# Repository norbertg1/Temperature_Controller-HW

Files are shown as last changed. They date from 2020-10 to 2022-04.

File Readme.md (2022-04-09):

# Temperature controller - HW

This is a temperature stabilizer (PID controller) for thermoelectric cooler (Peltier module) or ceramic heater modul based on STM32F3 microprocessor and buck converter. The repository consist from a project of **schematic** and **PCB design** files made in Altium Designer. All parts includes LCSC part number ready for manufacturing with JLCPCB.

See also:\
[Temperature controller firmware](https://github.com/norbertg1/Temperature_Controller-FW)\
[Temperature controller software](https://github.com/norbertg1/Temperature_Controller-SW)

**Features:**
 - 1.5 A and 5 A output current
 - Various NTC, PTC temp. sensor support
 - 16 bit ADC for temp. sensor
 - I2C temp. sensor support (BMP280, etc..)
 - Current, voltage and power sense for both outputs
 - PID loop
 - STM32F373
 - Vref with LM4041 1.225 V for better temp. sensing
 - OLED screen SSD1306
 - Control over serial port with PC

### Block schematic:

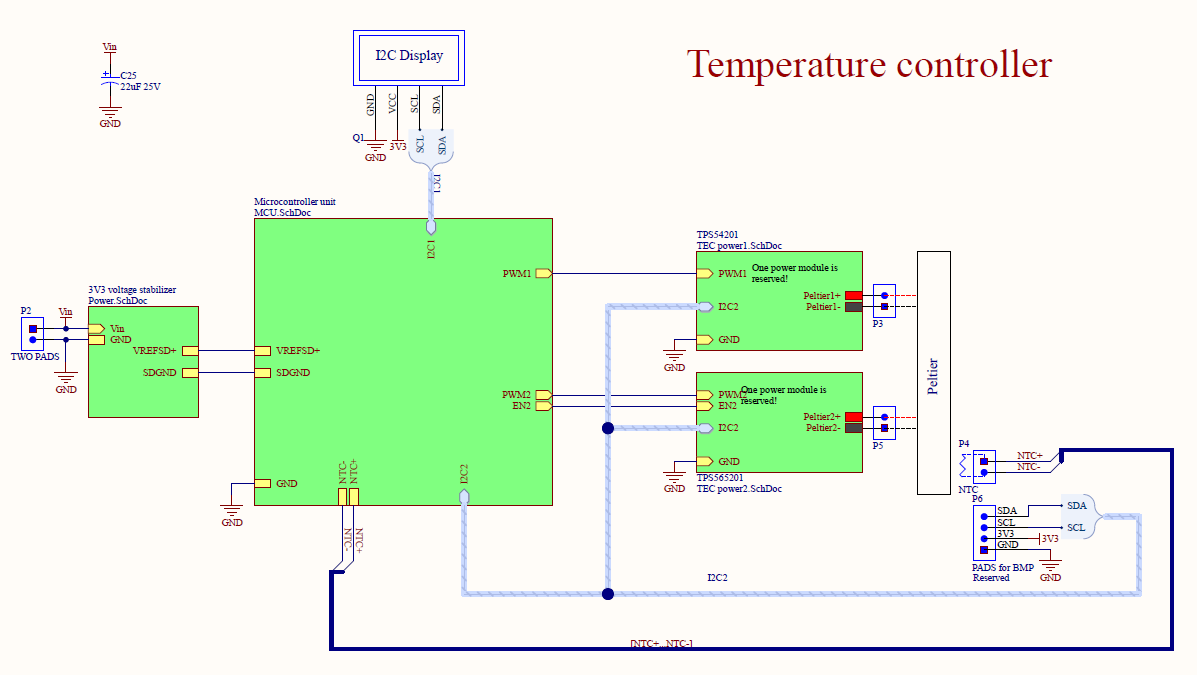
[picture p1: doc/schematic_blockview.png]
 \
Detailed hardware schematic [here](/doc/Temperature_controller.pdf).
### Use case

Original purpose for this project was cooling or heating and very precise stabilizing radiation detector and preamp input FET temperature, but its can be reused for anything else where the cooling or heating power is enough.

### Output power

The circuit is designed with two outputs:
 - **TPS54200**
Maximum output current is 1.5 A. Use this for less cooling power required applications, with more precious temp. control.
 - **TPS56201**
Maximum output current is 5 A. For utilizing the whole amount of this current need to replace the inductor with bigger one, with this one the maximum current is about somewhere 2-3 A.See datasheets and parameters.xlsx for exact components.

All the two ouputs are equiped with current sense shunt and current sense amplifier (INA226) communicating through I2C.

### Temperature sensing

Two options:
 - **BMP280:** Fully digital readout over I2C. Disadvantage is that you need 4 wires, and maximum and minimum values are determined by datasheet (-40 °C and 85 °C).

 - **PTC, NTC:** Precise 1.225 V is produced by IC for Vref and for power Rx and NTC modules. Differential ADC used for mesure the voltage of Rx and NTC modules. From the included temperature vs. resistance (R-T) table the temperature can be determined.
Also any part can be used that withstand the temperature and the R-T curve is known or measured.

### Programming

Programming through SWD connector with STlink v2:\

SWDIO — SWDIO\
SWCLK — SWCLK\
GND — GND

### Control loop
In very short:\
Read the temperature --> calculate the error from desired temp --> adjust the output power\
For software see the [related repository](https://github.com/xnorbi/Temperature_Controller-SW).

### Assembled PCB



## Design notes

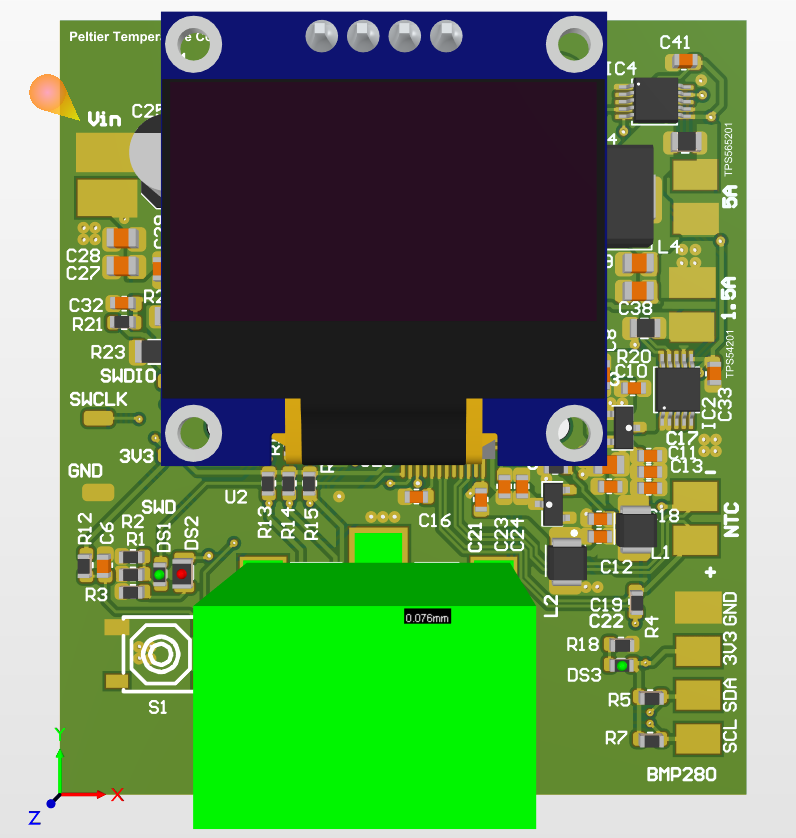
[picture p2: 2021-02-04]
doc/PCB_altium3D.png

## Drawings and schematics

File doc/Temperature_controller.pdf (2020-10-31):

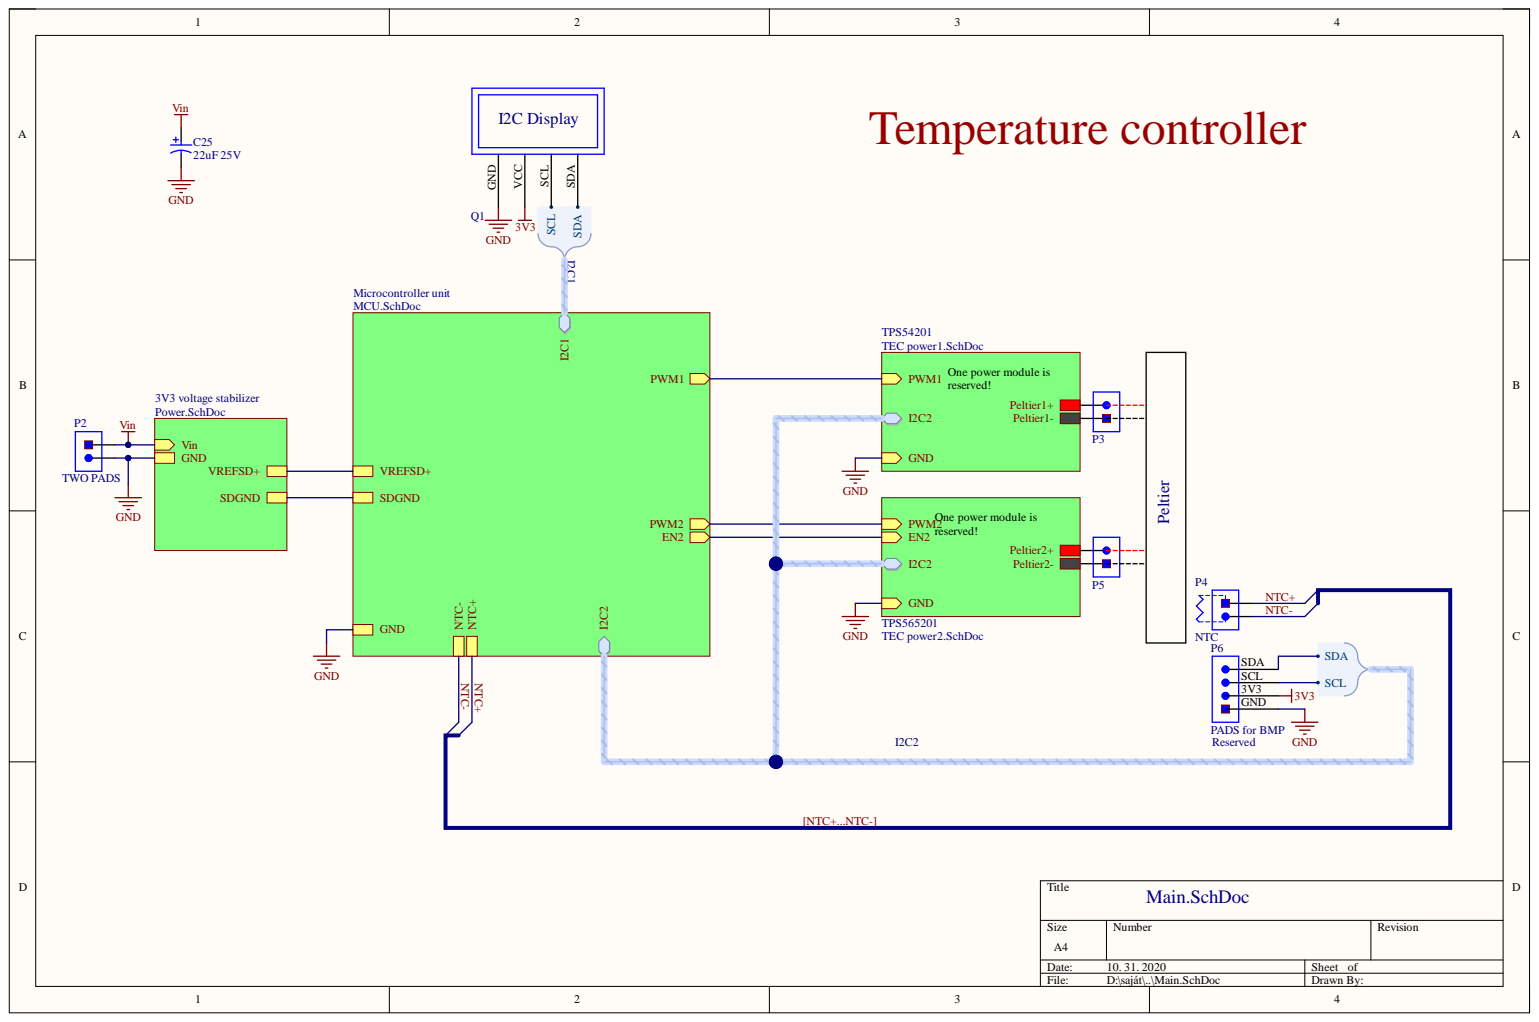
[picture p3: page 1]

One power module is
reserved!

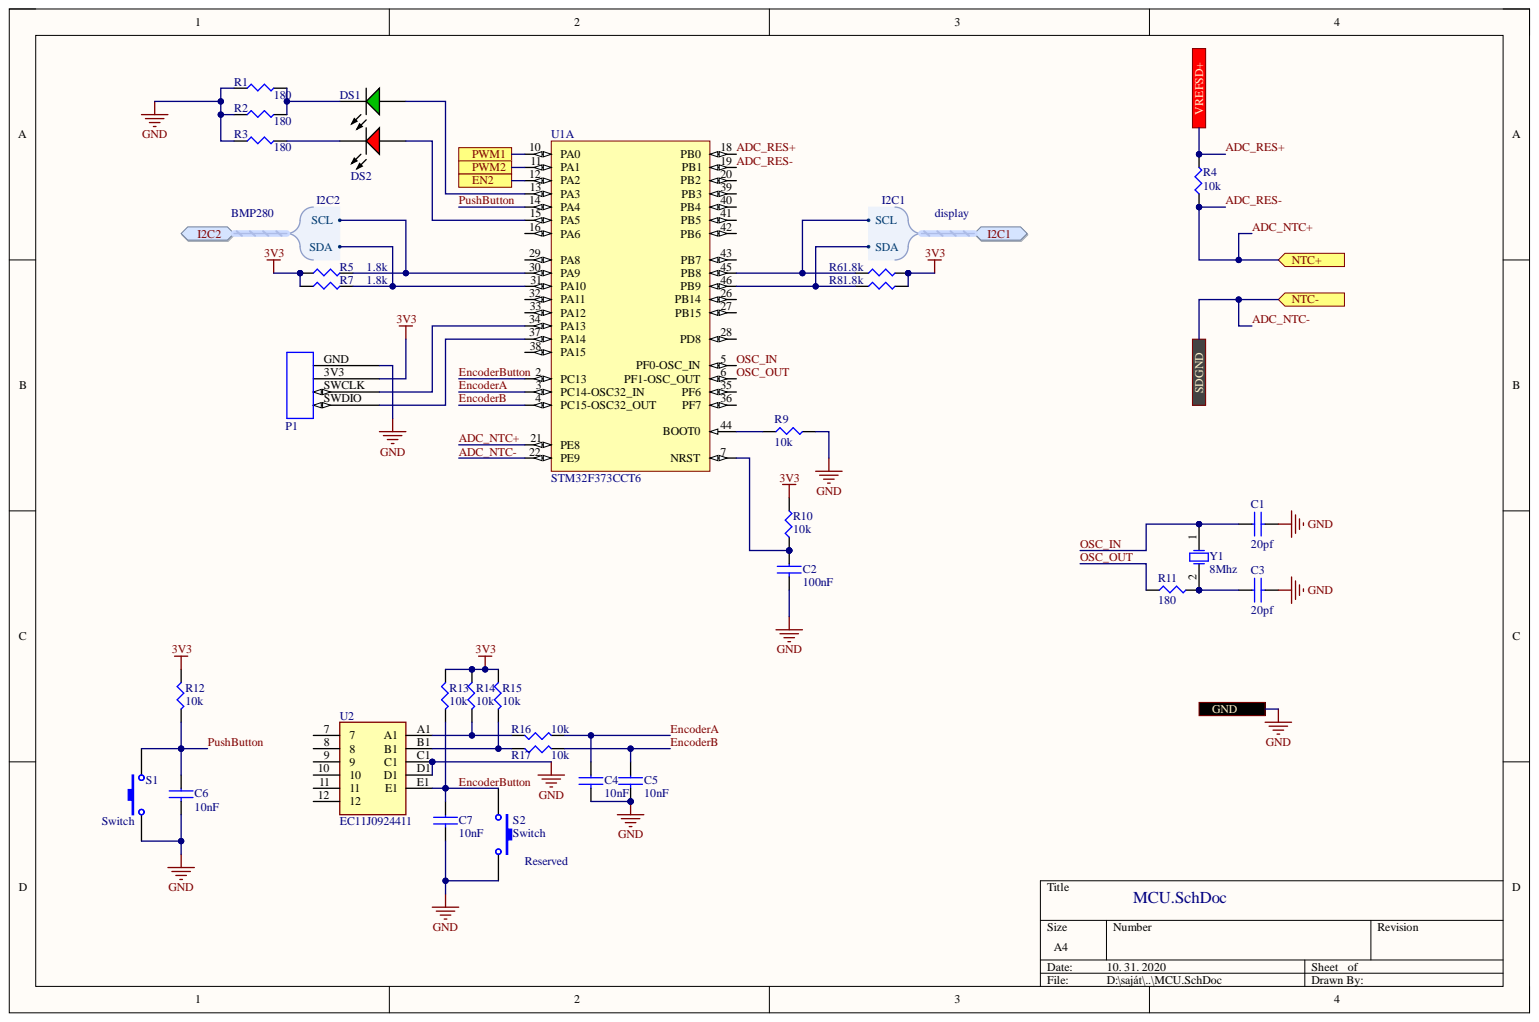
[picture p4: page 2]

EncoderButton

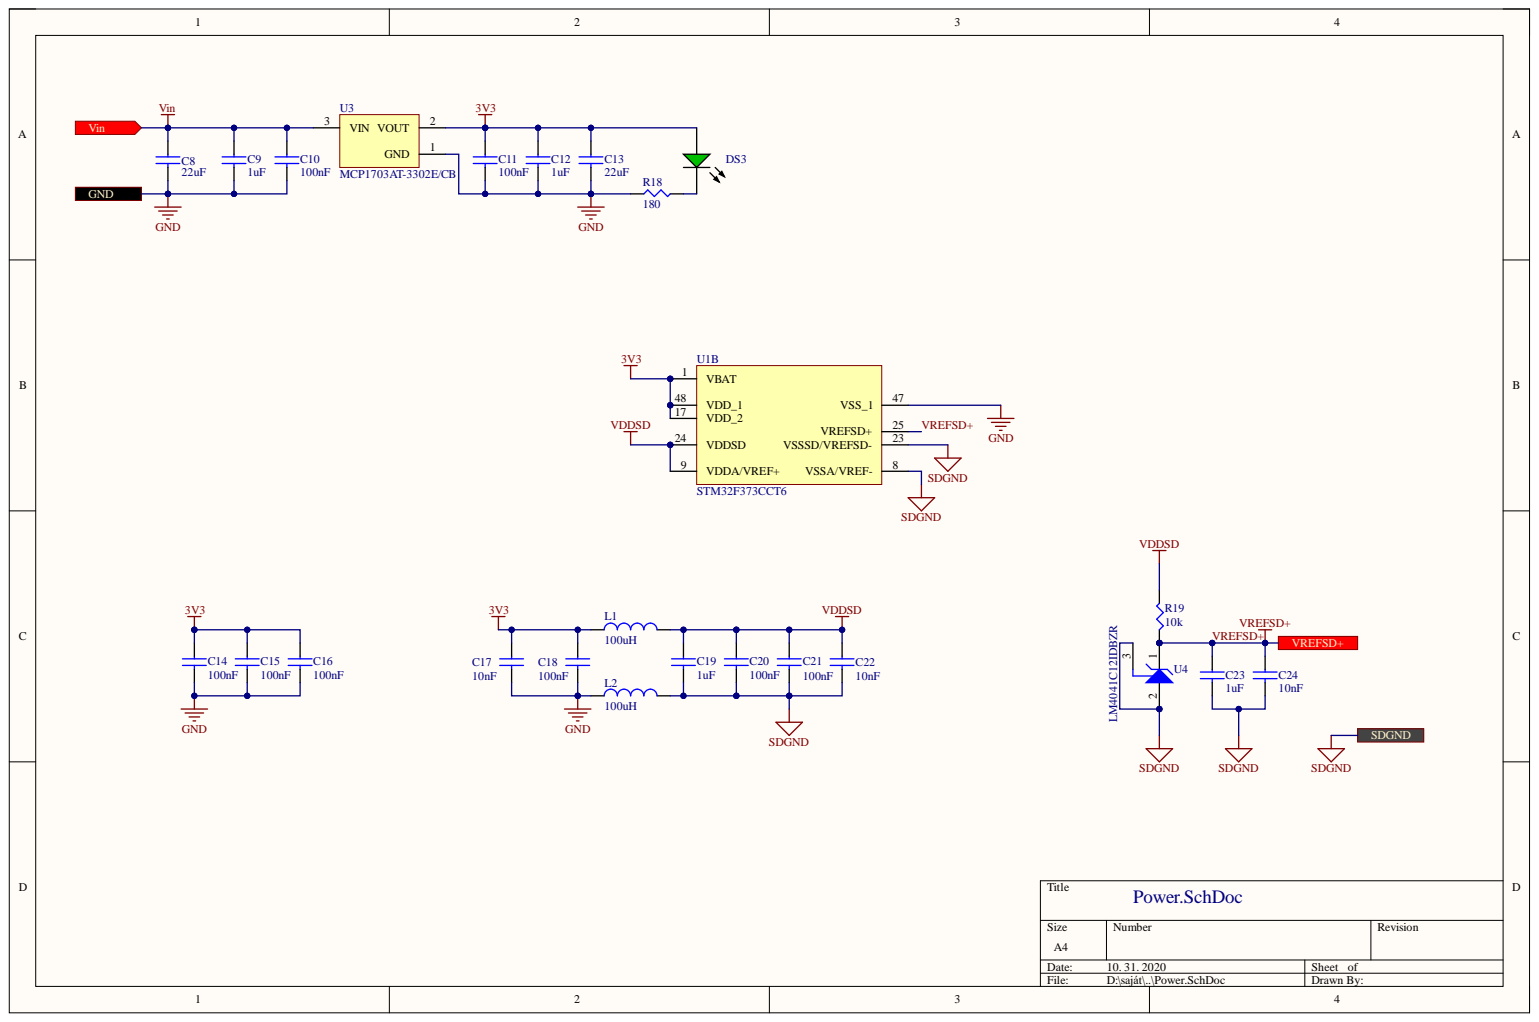
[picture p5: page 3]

VDD_2 17 VDD_1 48

VDDSD 24

VDDA/VREF+ 9

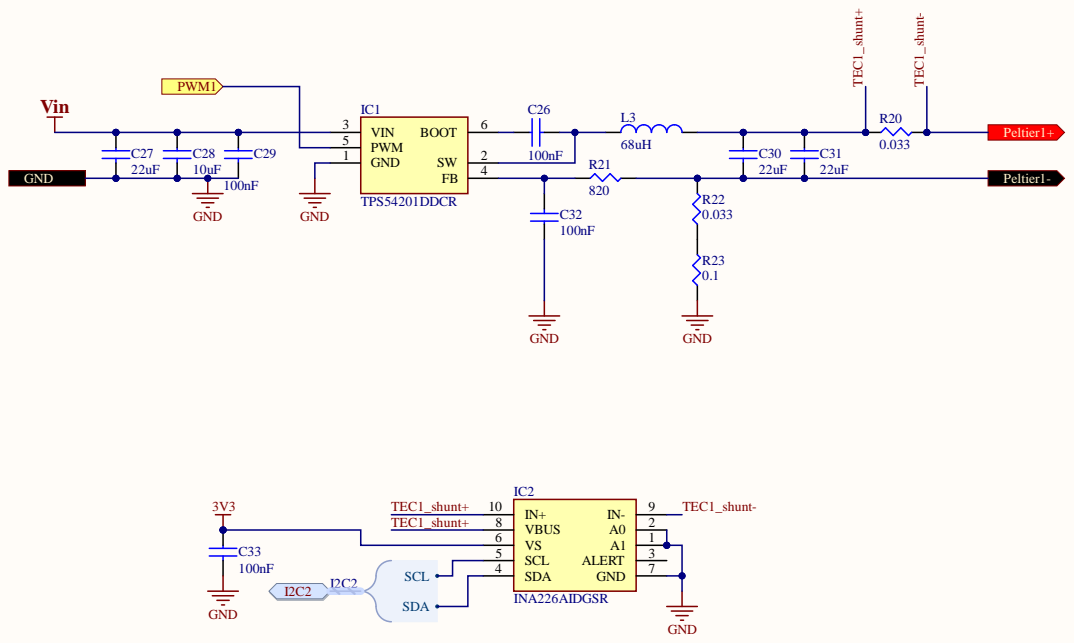
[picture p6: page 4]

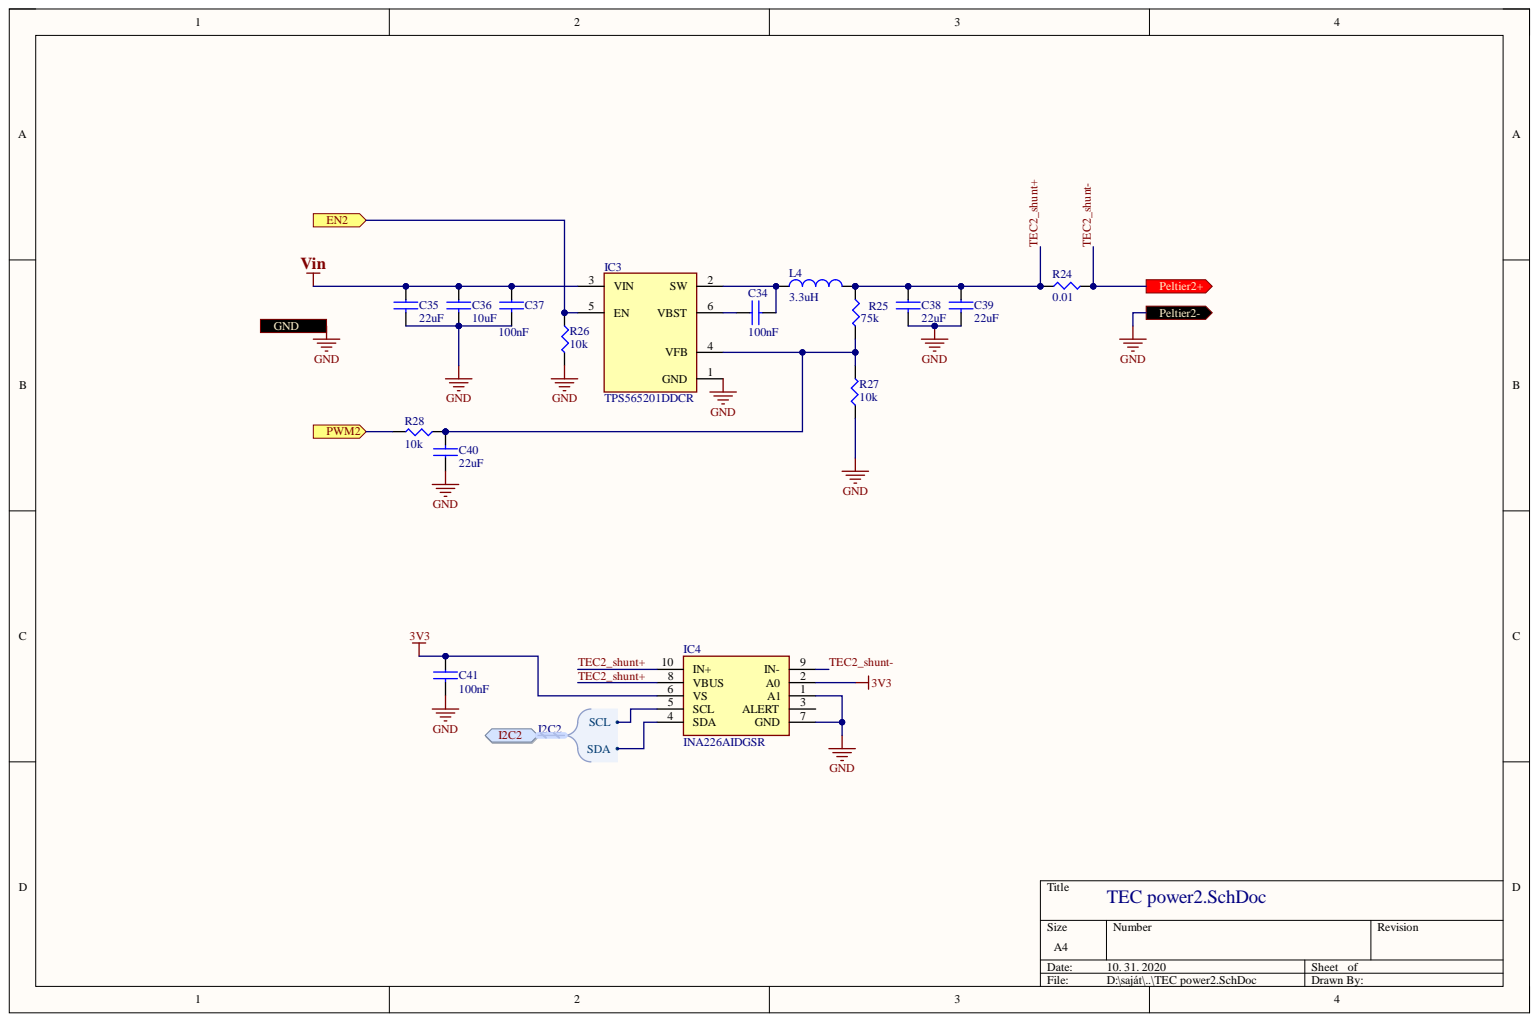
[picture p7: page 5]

C35 C36 C37
22uF | 10uF 100nF | R26 10k

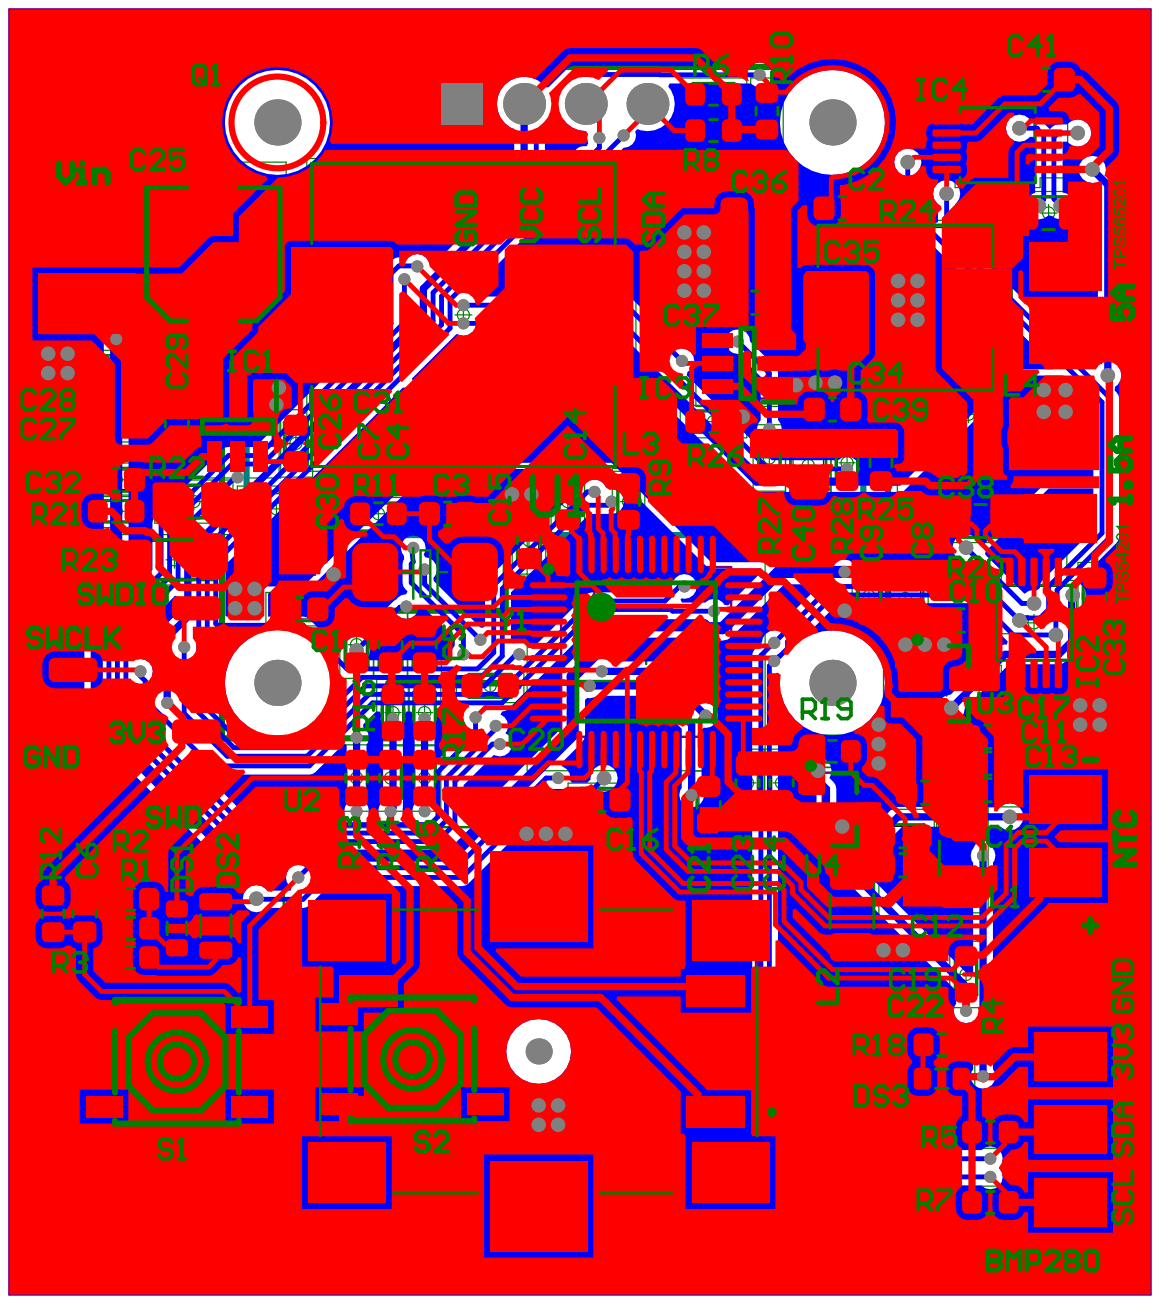
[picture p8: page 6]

Comment | Quantity | Designator | LCSC Part # | Footprint | Description | LibRef
100nF | 16 | C2, C10, C11, C14, C15, C16, C18, C20, C21, C26, C29, C32, C33, C34, C37, C41 | C14663 | CAPC160X80X90L35N | | capacitor
10k | 13 | R4, R9, R10, R12, R13, R14, R15, R16, R17, R19, R26, R27, R28 | C25804 | RESC160X80X90L30N | | Resistor
22uF | 9 | C8, C13, C27, C30, C31, C35, C38, C39, C40 | C45783 | CAPC200X125X110L50N | | capacitor
10nF | 7 C4, C5, C6, C7, C17, | C22, C24 | C57112 | CAPC160X80X90L35N | | capacitor
180 | 5 R1, R2, R3, R11, R18 | | C22828 | RESC160X80X90L30N | | Resistor
1uF | 4 C9, C12, C19, C23 | | C15849 | CAPC160X80X90L35N | | capacitor
1.8k | 4 R5, R6, R7, R8 | | C4177 | RESC160X80X90L30N | | Resistor
0.033 | 2 R20, R22 | | C127689 | RESC200X125X70L40N | | Resistor
10uF | 2 C28, C36 | | C15850 | CAPC200X125X110L50N | | capacitor
19-217/GHC-YR1S2/3T | 2 DS1, DS3 | | C72043 | LEDC160X80X60L30N | Green LED | LED
20pf | 2 C1, C3 | | C1648 | CAPC160X80X90L35N | | capacitor
100uH | 2 L1, L2 | | C333986 | INDC320X160X210L60N | Inductor | Inductor
INA226AIDGSR | 2 IC2, IC4 | | C49851 | SOP10P50_300X490X110L55X22N | Integrated Circuit | INA226AIDGSR
Switch | 2 S1, S2 | | | Tactile switch | Switch | Switch
TWO PADS for TEC | 2 P3, P5 | | | TWO PADS | | TWO PADS for TEC
#NAME? | 1 C25 | | C249771 | PNSC-FP-V-C_V | Aluminum Electrolytic Capacitor, 22 uF, +/-20%, 25 V, 2-Pin SMD (Size Code C), -55 to 105 degC, RoHS, Tape and Reel | CMP-2000-06213-1

0.01 | 1 R24 | | C127689 | RESC200X125X70L40N | | Resistor
0.1 | 1 R23 | | C25334 | RESC310X152X65L45N | | Resistor
3.3uH | 1 L4 | | C280586 | INDM730X660X300L160X290N | Inductor | Inductor
8Mhz | 1 Y1 | | C115962 | 5032 | Crystal Oscillator | XTAL
68uH | 1 L3 | | C169377 | INDM1250X1250X800L290X540N | Inductor | Inductor
75k | 1 R25 | | C46216 | RESC160X80X90L30N | | Resistor
820 | 1 R21 | | C23253 | RESC160X80X90L30N | | Resistor
EC11J0924411 | 1 U2 | | | EC11J0924411 | Rotary encoder | EC11J0924411
FC-2012HRK-620D | 1 DS2 | | C84256 | LEDC200X125X110L30N | Red LED | RED LED
LM4041C12IDBZR | 1 U4 | | C133587 | DBZ0003A_N | Precision Micropower Shunt Voltage Reference, 0.5% accuracy, 1.2 V, 15 ppm / degC, 12 mA, -40 to 85 degC, 3-pin SOT-23 (DBZ), Green (RoHS & no Sb/Br) | CMP-0366-00994-2
MCP1703AT-3302E/CB | 1 U3 | | C144183 | SOT-23A-CB3_M | | CMP-0136-00758-1
NTC | 1 P4 | | | TWO PADS | | TWO PADS for NTC
PADS for BMP | 1 P6 | | | FOUR PADS | | PADS for BMP
SSD1306OLED_big | 1 Q1 | | | SSD1306OLED | I2C display | SSD1306OLED_big
STM32F373CCT6 | 1 U1 | | C89403 | STM-LQFP48_L | ARM Cortex-M4 32-bit MCU, 256 KB Flash, 32 KB Internal RAM, 36 I/Os, 48-pin LQFP, -40 to 85 degC, Tray | STM32F373CCT6
SWD | 1 P1 | | | SWD | | SWD port
TPS54201DDCR | 1 IC1 | | | SOT95P280X110-6N | Integrated Circuit | TPS54201DDCR_1
TPS565201DDCR | 1 IC3 | | | SOT95P280X110-6N | Integrated Circuit | TPS565201DDCR
TWO PADS | 1 P2 | | | TWO PADS - medium | | TWO PADS

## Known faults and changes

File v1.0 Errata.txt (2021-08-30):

SWDIO and SWCLK swapped	✔2020.11.20
crystal change to 32 Mhz ---> not necessary google for benefits
LM4041 wrong footprint
R25 wrong part number its below 1ohm

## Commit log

2020-10-13 Initial commit. Crystal, reset, boot0 part of the schematic is completed.
    [Temperature_controller.PrjPcb, temperature_controller.PcbDoc, temperature_controller.SchDoc]
2020-10-14 The schematic is almost complete.
    [MCU.SchDoc, Power.SchDoc, TEC power.SchDoc, Temperature_controller.PrjPcb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]
2020-10-23 Design changed to hierarchical, TPS565201 device added.
    [Book1.xlsx, MCU.SchDoc, Main.SchDoc, Power.SchDoc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]
2020-10-23 Schematic completed.
    [MCU.SchDoc, Main.SchDoc, Power.SchDoc, TEC power.SchDoc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]
2020-10-24 PCB design in progress.
    [MCU.SchDoc, Main.SchDoc, Power.SchDoc, TEC power1.SchDoc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]
2020-10-25 All components are placed on PCB.
    [MCU.SchDoc, Main.SchDoc, Power.SchDoc, Temperature_controller.PrjPcb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]
2020-10-26 Routing and component palcement roughly completed.
    [MCU.SchDoc, Main.SchDoc, Power.SchDoc, Temperature_controller.PrjPcb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]
2020-10-27 Top overlay positioning completed, added ADC for NTC resistor (capability to measure current through NTC).
    [MCU.SchDoc, Power.SchDoc, Temperature_controller.PrjPcb, temperature_controller.PcbDoc]
2020-10-30 Impemented output power monitoring with INA226.
    [MCU.SchDoc, Main.SchDoc, Power.SchDoc, TEC power1.SchDoc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]
2020-10-31 Final optimizations before manufacturing. Extra button added.
    [MCU.SchDoc, Main.SchDoc, Power.SchDoc, TEC power1.SchDoc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]
2020-11-02 Files were sent to the factory. L1 and L2 inductor changed to 1210, other very small changes.
    [Power.SchDoc, TEC power1.SchDoc, Temperature_controller.PrjPcb, temperature_controller.PcbDoc]
2020-11-19 Readme and some pics added.
    [Book1.xlsx, Temperature_controller.PrjPcb, parameters.xlsx, temperature_controller.PcbDoc]
2020-11-20 SWDIO and SWCLK was swapped.
    [MCU.SchDoc, Temperature_controller.PrjPcb, temperature_controller.PcbDoc]
2020-12-30 Some lines added to errata
    [Temperature_controller.PrjPcb]
2021-02-04 New render picture added from Altium.
    [NTC_RESvsTEMP.xlsx]
2021-08-06 Comment message on schematic to add filter cap on ADC part.
    [MCU.SchDoc, Temperature_controller.PrjPcb, temperature_controller.PcbDoc]
